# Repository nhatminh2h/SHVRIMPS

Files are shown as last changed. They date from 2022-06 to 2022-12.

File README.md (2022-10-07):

# SHVRIMPS: Synchronised High-Voltage aRbItrary Modular Power Supply

SHVRIMPS is a high-voltage generator and optical imaging setup, capable of
- Outputting arbitrary high-voltage waveforms with an amplitude of 15 kV and a rise time less than 10 ms for load resistances below 8 MΩ.
- Eight independent synchronous and asynchronous 16-bit output channels.
- Monitoring the output high voltages and currents at adjustable sampling rate. Maximum rate of 9875 samples per second.
- Recording video of samples at a rate of 120 fps at 640x480 pixels.
- Displaying live video feed, control panel, and monitoring data on a GUI, accessible over Ethernet.



It consists of three main components: 1) an imaging system based on a Raspberry Pi 4B with a camera, producing a live video stream 2) a DAQ board compatible with either Arduino Nano 33 BLE or ESP32 DevKitC, and c) a multi-channel arbitrary waveform HV supply.

The repository is structured as follows:
- demonstration: videos and matlab figures
- diagrams: block diagrams of the entire setup and individual components
- hardware: KiCAD files showing the PCB design files
- setup: setup files
- software: source files for the Pi and DAQ board

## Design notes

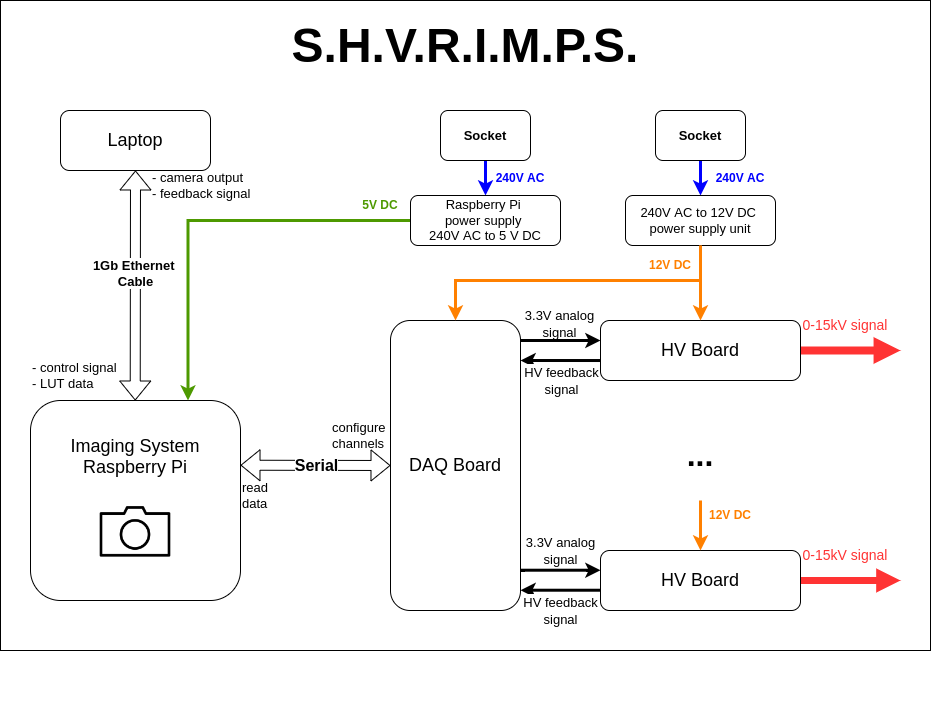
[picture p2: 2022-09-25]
diagrams/General_overview.png

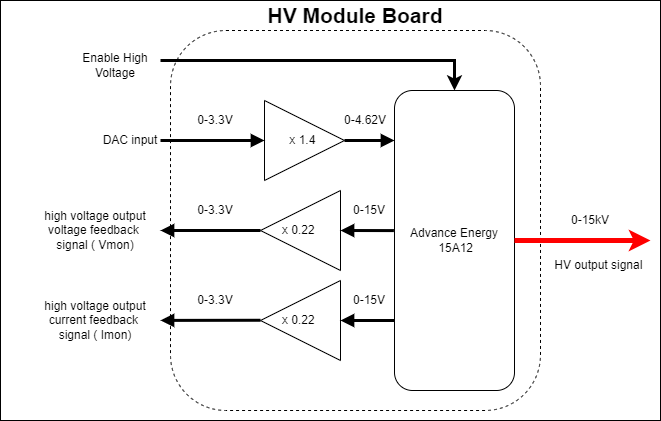
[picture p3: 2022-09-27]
diagrams/HV_module.drawio.png

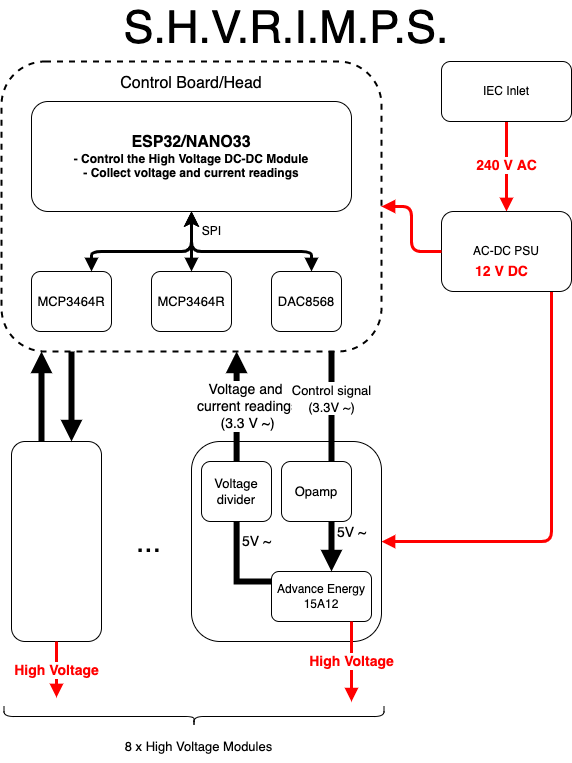
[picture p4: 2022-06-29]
diagrams/SHVRIMPS.png

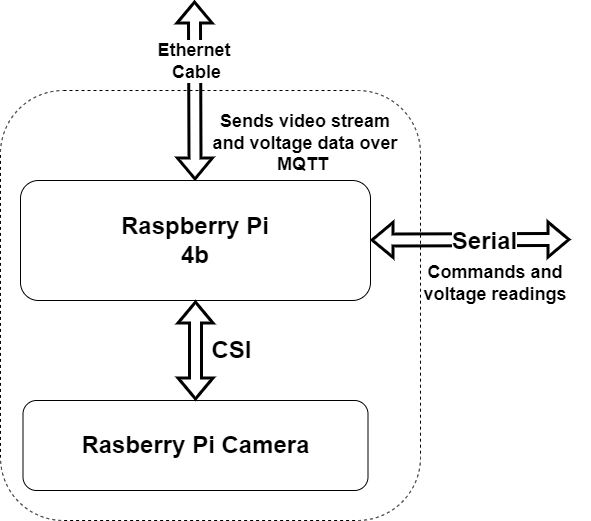
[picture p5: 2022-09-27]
diagrams/Imaging_system.drawio.png

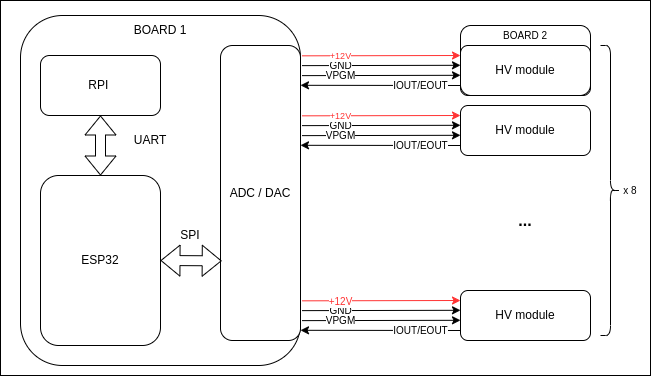
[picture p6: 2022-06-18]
diagrams/diagram.drawio.png

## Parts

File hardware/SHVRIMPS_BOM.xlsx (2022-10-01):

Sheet: DAQ Module
Ref | Qnty | Value | Description | Vendor | Manufacture number | Alternative Option | Unit Price | Total Price
A1, | 1 | Arduino_Nano_v3.x | Arduino Nano 33 BLE | https://uk.rs-online.com/web/p/arduino/1927587 | ABX00030 |  | £25.86 | £25.86
C1, C2, C4, C5, C6, C7, C11, C15, C16, C17, C18, C20, C22, | 13 | 0.1uF | Capacitor_SMD_0805 | https://www.mouser.co.uk/ProductDetail/Vishay-Vitramon/VJ0805Y104JXAMR | VJ0805Y104JXAMR | SMD components of same value | £0.34 | £4.47
C3, C8, C9, C19, C21, | 5 | 10uF | Capacitor_SMD_0806 | https://www.mouser.co.uk/ProductDetail/KYOCERA-AVX/0805ZD106KAT2A?qs=yeMJfaiNeLw5cKDoZRokwQ%3D%3D | 0805ZD106KAT2A | SMD components of same value | £0.18 | £0.88
C10, C12, | 2 | 2.2uF | Capacitor_SMD_0807 | https://www.mouser.co.uk/ProductDetail/KEMET/C0805C225K3RACAUTO |  | SMD components of same value | £0.24 | £0.49
C13, | 1 | 1nF | Capacitor_SMD_0808 | https://www.mouser.co.uk/ProductDetail/KYOCERA-AVX/08055A102JAT2A?qs=zdK0ZDdZmgzNLTxlxqGBmA%3D%3D |  | SMD components of same value | £0.11 | £0.11
C14, | 1 | 1uF | Capacitor_SMD_0809 | https://www.mouser.co.uk/ProductDetail/KYOCERA-AVX/0805DC105KAT2A |  | SMD components of same value | £0.18 | £0.18
D1, | 1 | SM4004 | 400V 1A General Purpose Rectifier Diode, MELF | https://eu.mouser.com/ProductDetail/Rectron/FM4004-W?qs=Iw9Ubr57Px3IHNH1bE4l9w%3D%3D | FM4004-W | SMD components of same value | £0.25 | £0.25
J1, | 1 | Conn_01x03_Male | Single row, 01x03, 2.54mm pitch | https://www.mouser.co.uk/ProductDetail/Molex/90136-1303?qs=kEwmkoUtv7SgZaNi9mb9yw%3D%3D | 90136-1303 | 2.54mm pitch connectors | £1.45 | £1.45
 | 1 | Conn_01x03_Female | Receptacle | https://www.mouser.co.uk/ProductDetail/Molex/90156-0143?qs=jBHU5RPckUpfJXnz3n%2F%2Fgw%3D%3D | 90156-0143 | 2.54mm pitch connectors | £0.54 | £0.54
J2, J3, J4, | 3 | Conn_02x08_Male | Double row, 02x08, 2.54mm pitch | https://www.mouser.co.uk/ProductDetail/Molex/90130-1316?qs=pAYFZ4D%2FDKtl%252BFLAfFoqpw%3D%3D | 90130-1316 | 2.54mm pitch connectors | £4.29 | £12.87
 | 3 | Conn_02x08_Female |  | https://www.mouser.co.uk/ProductDetail/Molex/90142-0016?qs=kEwmkoUtv7Tg2H5guvFtvw%3D%3D | 90142-0016 | 2.54mm pitch connectors | £1.24 | £3.72
J5, | 1 | Conn_01x02_Male | Single row, 01x02, 2.54mm pitch | https://www.mouser.co.uk/ProductDetail/Molex/90136-1202?qs=zF2Np9wwC%252B7fqKXQTHeKiQ%3D%3D | 90136-1202 | 2.54mm pitch connectors | £1.14 | £1.14
 | 1 | Conn_01x02_Female |  | https://www.mouser.co.uk/ProductDetail/Molex/90156-0142?qs=jBHU5RPckUotmv8DXiRxUw%3D%3D | 90156-0142 | 2.54mm pitch connectors | £0.39 | £0.39
R1, R3, R4, | 3 | 0 Ohm | Resistor_SMD_0803 | https://www.mouser.co.uk/ProductDetail/Vishay-Dale/CRCW08050000Z0EAC?qs=E3Y5ESvWgWMnvHb9ZvShmA%3D%3D | CRCW08050000Z0EAC | SMD components of same value | £0.08 | £0.25
R2, | 1 | 50 Ohm | Resistor_SMD_0804 | https://uk.farnell.com/panasonic/era6aeb49r9v/res-0805-49r9-0-125w-metal-film/dp/1810372 | ERA6AEB49R9V | SMD components of same value | £0.25 | £0.25
R5, R6, | 2 | 100k Ohm | Resistor_SMD_0805 | https://www.mouser.co.uk/ProductDetail/Vishay-Dale/RCS0805100KFKEA?qs=NKmfXavxMay%252BH0mbX9hKBw%3D%3D |  | SMD components of same value | £0.20 | £0.40
U1, | 1 | ESP32-DevKit-C | Alternative microcontroller: ESP32-devkitC-v4 |  |  |  |  | £0.00
U2, | 1 | LM7805_TO220 | Positive 1A 35V Linear Regulator, Fixed Output 5V, TO-220-3 | https://uk.farnell.com/stmicroelectronics/l7805abv/ic-v-reg-5v/dp/1467758?st=7805 | L7805ABV |  | £0.72 | £0.72
U3, | 1 | MCP1754S-3302xCB | Fixed 150mA Low Dropout Voltage Regulator, Positive, 3.3V output, SOT-23 | https://uk.rs-online.com/web/p/voltage-regulators/7559521 | MCP1754ST-3302E/CB | LDO with the same specification and footprint(make note of the pin out as different manufacturers have different ordering). | £0.45 | £0.45
U4, | 1 | MCP1825S-3.3V | 500mA, Low-Voltage, Low Quiescent Current LDO Regulator, SOT-223-3 | https://www.mouser.co.uk/ProductDetail/Microchip-Technology-Atmel/MCP1825ST-3302E-DB?qs=gsqZ4L1luKpq7RsgmIaiQQ%3D%3D | MCP1825ST-3302E/DB | LDO with the same specification and footprint(make note of the pin out as different manufacturers have different ordering). | £0.58 | £0.58
U5, | 1 | MCP1501-33xSN | 3.3V, 0.1%, 20mA, Precision Voltage Reference, SOIC-8 | https://uk.farnell.com/microchip/mcp1501-30e-sn/voltage-ref-series-3v-nsoic-8/dp/2524552?st=mcp1501 | MCP1501-30E/SN | LDO with the same specification and footprint(make note of the pin out as different manufacturers have different ordering). | £1.29 | £1.29
U6, U7, | 2 | MCP3464R | TSSOP-20_4.4x6.5mm_P0.65mm | https://www.mouser.co.uk/ProductDetail/Microchip-Technology/MCP3464R-E-ST?qs=W%2FMpXkg%252BdQ5bjobVCBkOgQ%3D%3D | MCP3464R-E/ST | MCP3x6x family | £4.38 | £8.76
U8, | 1 | DAC8568IAPW | TSSOP-16- | https://www.mouser.co.uk/ProductDetail/Texas-Instruments/DAC8568IAPW?qs=JxdSYA%2FPj%252BEQdFVS13frJg%3D%3D | DAC8568IAPW | DAC856x family | £21.65 | £21.65
X1, | 1 | ECS-2520MVLC-049-BN-TR | HCMOS Crystal Clock Oscillator, 2.5x2.0 mm SMD | https://www.mouser.co.uk/ProductDetail/ECS/ECS-2520MVLC-049-BN-TR?qs=DPoM0jnrROWa%252BbOCdP2Nhw%3D%3D | ECS-2520MVLC-049-BN-TR | Oscillator with frequency under 20 MHz and similar footprint. | £1.17 | £1.17
 | 1 | PCB | 4-Layer PCB | JLC-PCB |  |  | £1.31 | £1.31
 | 1 | PCB Stencil | Thin sheet of metal masking for solder paste application | JLC-PCB |  |  | £10
 |  |  |  |  |  |  | Total | £89.18

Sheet: HV Board
NOTE: The following BOM is for ONE high voltage module
Ref | Qnty | Value | Description | Vendor | Manufacture number | Alternative Option | Unit Price | Total Price
C1, C2, C3 | 3 | 0.1uF | Unpolarized capacitor | https://www.mouser.co.uk/ProductDetail/Vishay-BC-Components/K104M10X7RF5UH5?qs=uwenMUmGrtfrBFUqL2dLRw%3D%3D |  |  | 0.193 | 0.579
D1, | 1 | TZX3V6A-TR | Zener diode | https://www.mouser.co.uk/ProductDetail/Vishay-Semiconductors/ZPY16-TR?qs=6Fe8ASSgjNtFiGayzk%2F7%252BQ%3D%3D |  |  | 0.319 | 0.319
D2, | 1 | LED | Light emitting diode | https://www.mouser.co.uk/ProductDetail/VCC/VAOL-3MAE2?qs=io7aH2hdVh6UJW4IWVOfMg%3D%3D |  |  | 0.462 | 0.462
J1, | 1 | Conn_02x05_Male | Single row, 02x05, 2.54mm pitch | https://www.mouser.co.uk/ProductDetail/Molex/90142-0010?qs=BLN8Q0P37WbAKoqIAY0hgw%3D%3D | 90142-0010 |  | 0.756 | 0.756
J1- | 1 | Conn_02x05_Female | Receptacle | https://www.mouser.co.uk/ProductDetail/Molex/90130-1210?qs=FqTglUE30jKws6eRab4Phg%3D%3D | 90130-1210 |  | 1.81 | 1.81
J3, | 1 | Conn_01x02_Male | Single row, 01x02, 2.54mm pitch | https://www.mouser.co.uk/ProductDetail/Molex/90136-1202?qs=zF2Np9wwC%252B7fqKXQTHeKiQ%3D%3D | 90136-1202 |  | 1.14 | 1.14
J3- | 1 | Conn_01x02_Female | Receptacle | https://www.mouser.co.uk/ProductDetail/Molex/90156-0142?qs=jBHU5RPckUotmv8DXiRxUw%3D%3D | 90156-0142 |  | 0.386 | 0.386
R1, | 1 | 4.7k | Resistor | https://www.mouser.co.uk/ProductDetail/YAGEO/MFR-25FBF52-4K7?qs=oAGoVhmvjhyEuU2iU0uA4w%3D%3D | MFR-25FBF52-4K7 |  | 0.025 | 0.025
R2, | 2 | 2k | Resistor | https://www.mouser.co.uk/ProductDetail/YAGEO/MFR-12FTF52-2K?qs=oAGoVhmvjhwaGCFyQGkulg%3D%3D | MFR-25FBF52-4K7 |  | 0.021 | 0.042
R3, | 1 | 10k | Resistor | https://www.mouser.co.uk/ProductDetail/YAGEO/MFR-12FTF52-10K?qs=oAGoVhmvjhzLlUYKKBtdYQ%3D%3D | MFR-12FTF52-10K |  | 0.084 | 0.084
R5, R7, | 2 | 390k | Resistor | https://www.mouser.co.uk/ProductDetail/Vishay-BC-Components/HVR2500003903FR500?qs=7DG%2Fna1Fp6tcZrbH7PbgIQ%3D%3D |  |  | 0.353 | 0.706
R6, R8, | 2 | 110k | Resistor | https://www.mouser.co.uk/ProductDetail/Vishay-Dale/CPF110K000FKEE6 |  |  | 0.664 | 1.328
U1, | 1 | LM7809_TO220 | Positive 1A 35V Linear Regulator, Fixed Output 9V, TO-220-3 | https://www.mouser.co.uk/ProductDetail/STMicroelectronics/L7809ABV?qs=arR7071FstcxVp1H1MGQ%2Fw%3D%3D | L7809ABV |  | 0.655 | 0.655
U2, | 1 | LM358 | Dual Low-Noise Operational Amplifiers, DIP-8 | https://www.mouser.co.uk/ProductDetail/Texas-Instruments/LM358AP?qs=Zu35EjizYSShld7Gr9Muww%3D%3D | LM358AP |  | 0.353 | 0.353
U3, | 1 | 15A12 | High Voltage DC-DC module | https://www.mouser.co.uk/ProductDetail/Advanced-Energy/15A12-P4?qs=BZBei1rCqCD%252BiPNKsMykyg%3D%3D |  | Other | 433.09 | 433.09
 | 1 | PCB | 2-Layer PCB | JLC-PCB |  |  | 2 | 2
 |  |  |  |  |  |  | Total | 443.735
 |  |  |  |  |  |  | Total for 8 boards | 3549.88

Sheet: Raspberry Pi + camera
Ref | Qnty | Value | Description | Vendor | Manufacture number | Alternative Option | Unit Price | Total Price
 | 1 |  | Raspberry Pi 4B | https://www.raspberrypi.com/products/raspberry-pi-4-model-b/ |  |  | £65 | £65
 | 1 |  | Pi Camera v2 | https://thepihut.com/products/raspberry-pi-camera-module?src=raspberrypi |  |  | £26 | £26
 | 1 |  | Pi Screen
 |  |  |  |  |  |  | Total | £91

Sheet: Wires and Consumables
Ref | Qnty | Value | Description | Vendor | Manufacture number | Alternative Option | Unit Price | Total Price
 | 1 | CHIPQUIK SMD291SN Lead Free Solder Paste, 35g Syringe | Solder paste | https://uk.rs-online.com/web/p/solder-pastes/1466194 |  |  | £40.25 | £40.25
 | 1 | CHIPQUIK SMD291 10g Lead Free Solder Flux Syringe | Solder Flux | https://uk.rs-online.com/web/p/solder-flux/1466649 |  |  | £16.88 | £16.88
 | 1 | Mueller Electric WI-M / Silicone Wire Series Black 0.82 mm² Hook Up Wire, 18 AWG, 7/59/.05 mm, 3.05m, Silicone | Wire for internal wiring | https://uk.rs-online.com/web/p/hook-up-wire/2431647 |  |  | £18.62 | £18.62
 |  |  |  |  |  |  | Total | £75.75

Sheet: Enclosure and Mains Supply
Ref | Qnty | Value | Description | Vendor | Manufacture number | Unit Price | Total Price

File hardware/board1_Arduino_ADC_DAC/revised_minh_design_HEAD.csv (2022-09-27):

Source: | /Users/user/SHVRIMPS/SHVRIMPS/hardware/board1_Arduino_ADC_DAC/revised_minh_design.kicad_sch
Date: | Saturday, 24 September 2022 at 17:24:06
Tool: | Eeschema (6.0.5-0)
Generator: | /Applications/KiCad/KiCad.app/Contents/SharedSupport/plugins/bom_csv_grouped_by_value.py
Component Count: | 45
Individual Components:
Item | Qty | Reference(s) | Value | LibPart | Footprint | Datasheet
 |  | A1 | Arduino_Nano_v3.x | MCU_Module:Arduino_Nano_v3.x | Module:Arduino_Nano | http://www.mouser.com/pdfdocs/Gravitech_Arduino_Nano3_0.pdf
 |  | C1 | 0.1uF | Device:C | Capacitor_SMD:C_0805_2012Metric_Pad1.18x1.45mm_HandSolder | ~
 |  | C2 | 0.1uF | Device:C | Capacitor_SMD:C_0805_2012Metric_Pad1.18x1.45mm_HandSolder | ~
 |  | C3 | 10uF | Device:C | Capacitor_SMD:C_0805_2012Metric_Pad1.18x1.45mm_HandSolder | ~
 |  | C4 | 0.1uF | Device:C | Capacitor_SMD:C_0805_2012Metric_Pad1.18x1.45mm_HandSolder | ~
 |  | C5 | 0.1uF | Device:C | Capacitor_SMD:C_0805_2012Metric_Pad1.18x1.45mm_HandSolder | ~
 |  | C6 | 0.1uF | Device:C | Capacitor_SMD:C_0805_2012Metric_Pad1.18x1.45mm_HandSolder | ~
 |  | C7 | 0.1uF | Device:C | Capacitor_SMD:C_0805_2012Metric_Pad1.18x1.45mm_HandSolder | ~
 |  | C8 | 10uF | Device:C | Capacitor_SMD:C_0805_2012Metric_Pad1.18x1.45mm_HandSolder | ~
 |  | C9 | 10uF | Device:C | Capacitor_SMD:C_0805_2012Metric_Pad1.18x1.45mm_HandSolder | ~
 |  | C10 | 2.2uF | Device:C | Capacitor_SMD:C_0805_2012Metric_Pad1.18x1.45mm_HandSolder | ~
 |  | C11 | 0.1uF | Device:C | Capacitor_SMD:C_0805_2012Metric_Pad1.18x1.45mm_HandSolder | ~
 |  | C12 | 2.2uF | Device:C | Capacitor_SMD:C_0805_2012Metric_Pad1.18x1.45mm_HandSolder | ~
 |  | C13 | 1nF | Device:C | Capacitor_SMD:C_0805_2012Metric_Pad1.18x1.45mm_HandSolder | ~
 |  | C14 | 1uF | Device:C | Capacitor_SMD:C_0805_2012Metric_Pad1.18x1.45mm_HandSolder | ~
 |  | C15 | 0.1uF | Device:C | Capacitor_SMD:C_0805_2012Metric_Pad1.18x1.45mm_HandSolder | ~
 |  | C16 | 0.1uF | Device:C | Capacitor_SMD:C_0805_2012Metric_Pad1.18x1.45mm_HandSolder | ~
 |  | C17 | 0.1uF | Device:C | Capacitor_SMD:C_0805_2012Metric_Pad1.18x1.45mm_HandSolder | ~
 |  | C18 | 0.1uF | Device:C | Capacitor_SMD:C_0805_2012Metric_Pad1.18x1.45mm_HandSolder | ~
 |  | C19 | 10uF | Device:C | Capacitor_SMD:C_0805_2012Metric_Pad1.18x1.45mm_HandSolder | ~
 |  | C20 | 0.1uF | Device:C | Capacitor_SMD:C_0805_2012Metric_Pad1.18x1.45mm_HandSolder | ~
 |  | C21 | 10uF | Device:C | Capacitor_SMD:C_0805_2012Metric_Pad1.18x1.45mm_HandSolder | ~
 |  | C22 | 0.1uF | Device:C | Capacitor_SMD:C_0805_2012Metric_Pad1.18x1.45mm_HandSolder | ~
 |  | D1 | SM4004 | Diode:SM4004 | Diode_SMD:D_MELF | http://cdn-reichelt.de/documents/datenblatt/A400/SMD1N400%23DIO.pdf
 |  | J1 | Conn_01x03_Male | Connector:Conn_01x03_Male | Connector_PinSocket_2.54mm:PinSocket_1x03_P2.54mm_Vertical | ~
 |  | J2 | Conn_02x08_Odd_Even | Connector_Generic:Conn_02x08_Odd_Even | Connector_PinSocket_2.54mm:PinSocket_2x08_P2.54mm_Vertical | ~
 |  | J3 | Conn_02x08_Odd_Even | Connector_Generic:Conn_02x08_Odd_Even | Connector_PinSocket_2.54mm:PinSocket_2x08_P2.54mm_Vertical | ~
 |  | J4 | Conn_02x08_Odd_Even | Connector_Generic:Conn_02x08_Odd_Even | Connector_PinSocket_2.54mm:PinSocket_2x08_P2.54mm_Vertical | ~
 |  | J5 | Conn_01x02_Male | Connector:Conn_01x02_Male | Connector_PinSocket_2.54mm:PinSocket_1x02_P2.54mm_Vertical | ~
 |  | R1 | 0 | Device:R | Resistor_SMD:R_0805_2012Metric_Pad1.20x1.40mm_HandSolder | ~
 |  | R2 | 50 | Device:R | Resistor_SMD:R_0805_2012Metric_Pad1.20x1.40mm_HandSolder | ~
 |  | R3 | 0 | Device:R | Resistor_SMD:R_0805_2012Metric_Pad1.20x1.40mm_HandSolder | ~
 |  | R4 | 0 | Device:R | Resistor_SMD:R_0805_2012Metric_Pad1.20x1.40mm_HandSolder | ~
 |  | R5 | 100k | Device:R | Resistor_SMD:R_0805_2012Metric_Pad1.20x1.40mm_HandSolder | ~
 |  | R6 | 100k | Device:R | Resistor_SMD:R_0805_2012Metric_Pad1.20x1.40mm_HandSolder | ~
 |  | TP1 | TestPoint | Connector:TestPoint | Connector_PinHeader_2.54mm:PinHeader_1x01_P2.54mm_Vertical | ~
 |  | U1 | ESP32-DevKit-C | design:ESP32-DevKit-C | Library:ESP32-devkitC-v4
 |  | U2 | LM7805_TO220 | Regulator_Linear:LM7805_TO220 | Package_TO_SOT_THT:TO-220-3_Vertical | https://www.onsemi.cn/PowerSolutions/document/MC7800-D.PDF
 |  | U3 | MCP1754S-3302xCB | Regulator_Linear:MCP1754S-3302xCB | Package_TO_SOT_SMD:SOT-23 | http://ww1.microchip.com/downloads/en/DeviceDoc/20002276C.pdf
 |  | U4 | MCP1825S-3.3V | Regulator_Linear:MCP1825S | Package_TO_SOT_SMD:SOT-223-3_TabPin2 | http://ww1.microchip.com/downloads/en/devicedoc/22056b.pdf
 |  | U5 | MCP1501-33xSN | Reference_Voltage:MCP1501-33xSN | Package_SO:SOIC-8_3.9x4.9mm_P1.27mm | http://ww1.microchip.com/downloads/en/DeviceDoc/20005474E.pdf
 |  | U6 | MCP3464R | design:MCP3464R | Package_SO:TSSOP-20_4.4x6.5mm_P0.65mm
 |  | U7 | MCP3464R | design:MCP3464R | Package_SO:TSSOP-20_4.4x6.5mm_P0.65mm
 |  | U8 | DAC8568IAPW | design:DAC8568IAPW | Package_SO:TSSOP-16-1EP_4.4x5mm_P0.65mm
 |  | X1 | ECS-2520MVLC-049-BN-TR | Oscillator:ECS-2520MV-xxx-xx | Oscillator:Oscillator_SMD_ECS_2520MV-xxx-xx-4Pin_2.5x2.0mm | https://www.ecsxtal.com/store/pdf/ECS-2520MV.pdf
Collated Components:
Item | Qty | Reference(s) | Value | LibPart | Footprint | Datasheet
1 | 1 | A1 | Arduino_Nano_v3.x | MCU_Module:Arduino_Nano_v3.x | Module:Arduino_Nano | http://www.mouser.com/pdfdocs/Gravitech_Arduino_Nano3_0.pdf
2 | 13 | C1, C2, C4, C5, C6, C7, C11, C15, C16, C17, C18, C20, C22 | 0.1uF | Device:C | Capacitor_SMD:C_0805_2012Metric_Pad1.18x1.45mm_HandSolder | ~
3 | 5 | C3, C8, C9, C19, C21 | 10uF | Device:C | Capacitor_SMD:C_0805_2012Metric_Pad1.18x1.45mm_HandSolder | ~
4 | 2 | C10, C12 | 2.2uF | Device:C | Capacitor_SMD:C_0805_2012Metric_Pad1.18x1.45mm_HandSolder | ~
5 | 1 | C13 | 1nF | Device:C | Capacitor_SMD:C_0805_2012Metric_Pad1.18x1.45mm_HandSolder | ~
6 | 1 | C14 | 1uF | Device:C | Capacitor_SMD:C_0805_2012Metric_Pad1.18x1.45mm_HandSolder | ~
7 | 1 | D1 | SM4004 | Diode:SM4004 | Diode_SMD:D_MELF | http://cdn-reichelt.de/documents/datenblatt/A400/SMD1N400%23DIO.pdf
8 | 1 | J1 | Conn_01x03_Male | Connector:Conn_01x03_Male | Connector_PinSocket_2.54mm:PinSocket_1x03_P2.54mm_Vertical | ~
9 | 3 | J2, J3, J4 | Conn_02x08_Odd_Even | Connector_Generic:Conn_02x08_Odd_Even | Connector_PinSocket_2.54mm:PinSocket_2x08_P2.54mm_Vertical | ~
10 | 1 | J5 | Conn_01x02_Male | Connector:Conn_01x02_Male | Connector_PinSocket_2.54mm:PinSocket_1x02_P2.54mm_Vertical | ~
11 | 3 | R1, R3, R4 | 0 | Device:R | Resistor_SMD:R_0805_2012Metric_Pad1.20x1.40mm_HandSolder | ~
12 | 1 | R2 | 50 | Device:R | Resistor_SMD:R_0805_2012Metric_Pad1.20x1.40mm_HandSolder | ~
13 | 2 | R5, R6 | 100k | Device:R | Resistor_SMD:R_0805_2012Metric_Pad1.20x1.40mm_HandSolder | ~
14 | 1 | TP1 | TestPoint | Connector:TestPoint | Connector_PinHeader_2.54mm:PinHeader_1x01_P2.54mm_Vertical | ~
15 | 1 | U1 | ESP32-DevKit-C | design:ESP32-DevKit-C | Library:ESP32-devkitC-v4
16 | 1 | U2 | LM7805_TO220 | Regulator_Linear:LM7805_TO220 | Package_TO_SOT_THT:TO-220-3_Vertical | https://www.onsemi.cn/PowerSolutions/document/MC7800-D.PDF
17 | 1 | U3 | MCP1754S-3302xCB | Regulator_Linear:MCP1754S-3302xCB | Package_TO_SOT_SMD:SOT-23 | http://ww1.microchip.com/downloads/en/DeviceDoc/20002276C.pdf
18 | 1 | U4 | MCP1825S-3.3V | Regulator_Linear:MCP1825S | Package_TO_SOT_SMD:SOT-223-3_TabPin2 | http://ww1.microchip.com/downloads/en/devicedoc/22056b.pdf
19 | 1 | U5 | MCP1501-33xSN | Reference_Voltage:MCP1501-33xSN | Package_SO:SOIC-8_3.9x4.9mm_P1.27mm | http://ww1.microchip.com/downloads/en/DeviceDoc/20005474E.pdf
20 | 2 | U6, U7 | MCP3464R | design:MCP3464R | Package_SO:TSSOP-20_4.4x6.5mm_P0.65mm
21 | 1 | U8 | DAC8568IAPW | design:DAC8568IAPW | Package_SO:TSSOP-16-1EP_4.4x5mm_P0.65mm
22 | 1 | X1 | ECS-2520MVLC-049-BN-TR | Oscillator:ECS-2520MV-xxx-xx | Oscillator:Oscillator_SMD_ECS_2520MV-xxx-xx-4Pin_2.5x2.0mm | https://www.ecsxtal.com/store/pdf/ECS-2520MV.pdf

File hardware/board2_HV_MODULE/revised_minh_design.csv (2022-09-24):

Source: | /Users/user/hvawg/board2_HV_MODULE/revised_minh_design.kicad_sch
Date: | Thursday, 30 June 2022 at 15:07:25
Tool: | Eeschema (6.0.5-0)
Generator: | /Applications/KiCad/KiCad.app/Contents/SharedSupport/plugins/bom_csv_grouped_by_value_with_fp.py
Component Count: | 18
Ref | Qnty | Value | Cmp name | Footprint | Description | Vendor
C1, C2, C3, | 3 | 0.1uF | C | Capacitor_THT:C_Disc_D6.0mm_W2.5mm_P5.00mm | Unpolarized capacitor
D1, | 1 | TZX3V6A-TR | D_Zener | Diode_THT:D_DO-35_SOD27_P7.62mm_Horizontal | Zener diode
D2, | 1 | LED | LED | LED_THT:LED_D3.0mm_Clear | Light emitting diode
J1, | 1 | Conn_01x07_Male | Conn_01x07_Male | Connector_PinSocket_2.54mm:PinSocket_1x07_P2.54mm_Vertical | Generic connector, single row, 01x07, script generated (kicad-library-utils/schlib/autogen/connector/)
J2, | 1 | Conn_01x01_Male | Conn_01x01_Male | Connector_Wire:SolderWire-0.75sqmm_1x01_D1.25mm_OD2.3mm_Relief | Generic connector, single row, 01x01, script generated (kicad-library-utils/schlib/autogen/connector/)
R1, R3, | 2 | 10k | R | Resistor_THT:R_Axial_DIN0207_L6.3mm_D2.5mm_P10.16mm_Horizontal | Resistor
R2, | 1 | 4.7k | R | Resistor_THT:R_Axial_DIN0207_L6.3mm_D2.5mm_P7.62mm_Horizontal | Resistor
R4, | 1 | 1K | R | Resistor_THT:R_Axial_DIN0207_L6.3mm_D2.5mm_P10.16mm_Horizontal | Resistor
R5, | 1 | 2K | R | Resistor_THT:R_Axial_DIN0207_L6.3mm_D2.5mm_P15.24mm_Horizontal | Resistor
R6, R8, | 2 | 1.1K | R | Resistor_THT:R_Axial_DIN0207_L6.3mm_D2.5mm_P10.16mm_Horizontal | Resistor
R7, | 1 | 2K | R | Resistor_THT:R_Axial_DIN0207_L6.3mm_D2.5mm_P10.16mm_Horizontal | Resistor
U1, | 1 | LM7805_TO220 | LM7805_TO220 | Package_TO_SOT_THT:TO-220-3_Vertical | Positive 1A 35V Linear Regulator, Fixed Output 5V, TO-220
U2, | 1 | NE5532 | NE5532 | Package_DIP:DIP-8_W7.62mm | Dual Low-Noise Operational Amplifiers, DIP-8/SOIC-8
U3, | 1 | CB101 | CB101 | Library:CB101

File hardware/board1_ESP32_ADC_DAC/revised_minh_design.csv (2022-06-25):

Source: | /Users/user/hvawg/board1_ESP32_ADC_DAC/revised_minh_design.kicad_sch
Date: | Friday, 24 June 2022 at 15:34:22
Tool: | Eeschema (6.0.5-0)
Generator: | /Applications/KiCad/KiCad.app/Contents/SharedSupport/plugins/bom_csv_grouped_by_value_with_fp.py
Component Count: | 34
Ref | Qnty | Value | Cmp name | Footprint | Description | Vendor
C1, C2, C4, C5, C6, C7, C11, C15, C16, C17, C18, | 11 | 0.1uF | C | Capacitor_SMD:C_0805_2012Metric_Pad1.18x1.45mm_HandSolder | Unpolarized capacitor
C3, C8, C9, | 3 | 10uF | C | Capacitor_SMD:C_0805_2012Metric_Pad1.18x1.45mm_HandSolder | Unpolarized capacitor
C10, C12, | 2 | 2.2uF | C | Capacitor_SMD:C_0805_2012Metric_Pad1.18x1.45mm_HandSolder | Unpolarized capacitor
C13, | 1 | 1nF | C | Capacitor_SMD:C_0805_2012Metric_Pad1.18x1.45mm_HandSolder | Unpolarized capacitor
C14, | 1 | 1uF | C | Capacitor_SMD:C_0805_2012Metric_Pad1.18x1.45mm_HandSolder | Unpolarized capacitor
J1, | 1 | Conn_01x03_Male | Conn_01x03_Male | Connector_PinSocket_2.54mm:PinSocket_1x03_P2.54mm_Vertical | Generic connector, single row, 01x03, script generated (kicad-library-utils/schlib/autogen/connector/)
J2, J3, J4, | 3 | Conn_01x08_Male | Conn_01x08_Male | Connector_PinSocket_2.54mm:PinSocket_1x08_P2.54mm_Vertical | Generic connector, single row, 01x08, script generated (kicad-library-utils/schlib/autogen/connector/)
R1, R3, | 2 | 0 | R | Resistor_SMD:R_0805_2012Metric_Pad1.20x1.40mm_HandSolder | Resistor
R2, | 1 | 50 | R | Resistor_SMD:R_0805_2012Metric_Pad1.20x1.40mm_HandSolder | Resistor
U1, | 1 | ESP32-DevKit-C | ESP32-DevKit-C | Library:ESP32-devkitC-v4
U2, | 1 | LM7805_TO220 | LM7805_TO220 | Package_TO_SOT_THT:TO-220-3_Vertical | Positive 1A 35V Linear Regulator, Fixed Output 5V, TO-220
U3, | 1 | MCP1754S-3302xCB | MCP1754S-3302xCB | Package_TO_SOT_SMD:SOT-23 | Fixed 150mA Low Dropout Voltage Regulator, Positive, 3.3V output, SOT-23
U4, | 1 | MCP1825S-3.3V | MCP1825S | Package_TO_SOT_SMD:SOT-223-3_TabPin2 | 500mA, Low-Voltage, Low Quiescent Current LDO Regulator, SOT-223, TO-220, TO-263
U5, | 1 | MCP1501-33xSN | MCP1501-33xSN | Package_SO:SOIC-8_3.9x4.9mm_P1.27mm | 3.3V, 0.1%, 20mA, Precision Voltage Reference, SOIC-8
U6, U7, | 2 | MCP3464R | MCP3464R | Package_SO:TSSOP-20_4.4x6.5mm_P0.65mm
U8, | 1 | DAC8568IAPW | DAC8568IAPW | Package_SO:TSSOP-16-1EP_4.4x5mm_P0.65mm
X1, | 1 | ECS-2520MVLC-049-BN-TR | ECS-2520MV-xxx-xx | Oscillator:Oscillator_SMD_ECS_2520MV-xxx-xx-4Pin_2.5x2.0mm | HCMOS Crystal Clock Oscillator, 2.5x2.0 mm SMD

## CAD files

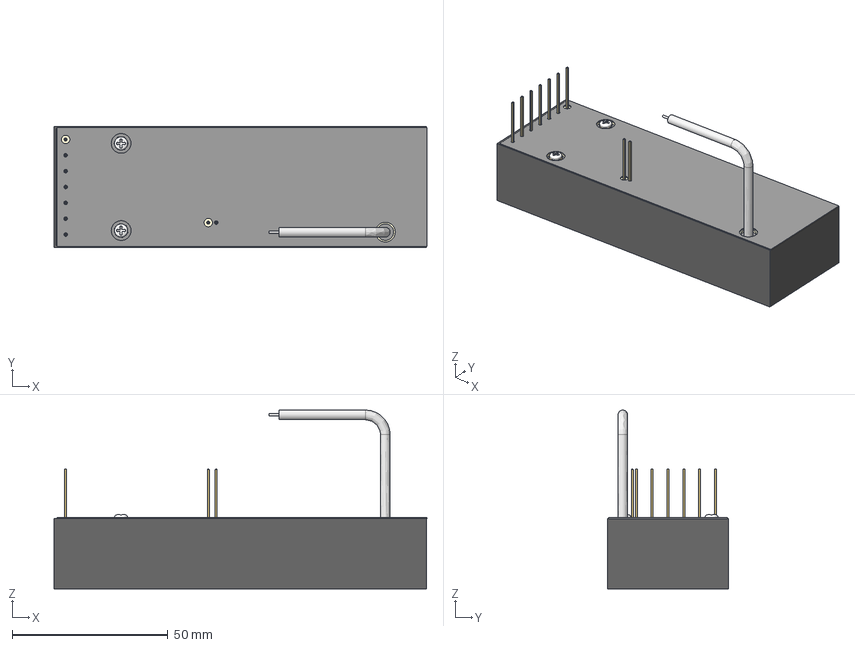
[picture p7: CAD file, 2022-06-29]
diagrams/OL-015_15A_STANDARD.stp
119.6 x 38.7 x 57.4 mm

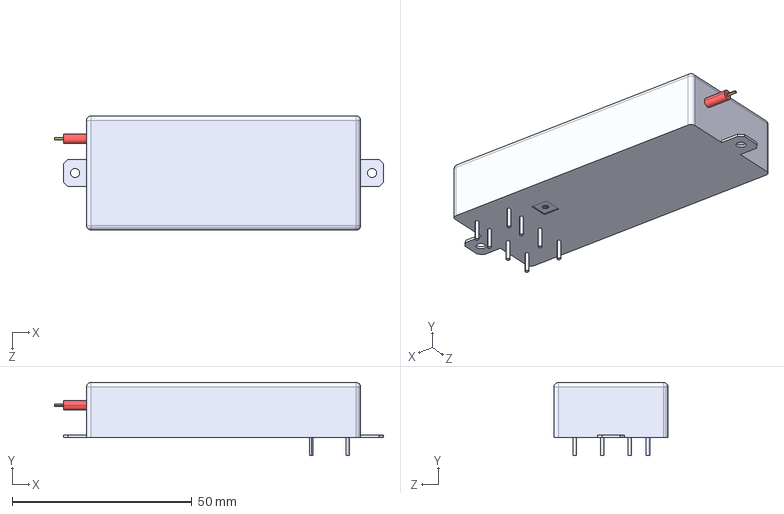
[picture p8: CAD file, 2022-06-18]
hardware/board1_Arduino_ADC_DAC/CB101.STEP
91.4 x 20.3 x 31.8 mm

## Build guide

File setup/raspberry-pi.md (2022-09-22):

nmap -n -sP 10.42.0.255/24
ssh pi@10.42.0.198

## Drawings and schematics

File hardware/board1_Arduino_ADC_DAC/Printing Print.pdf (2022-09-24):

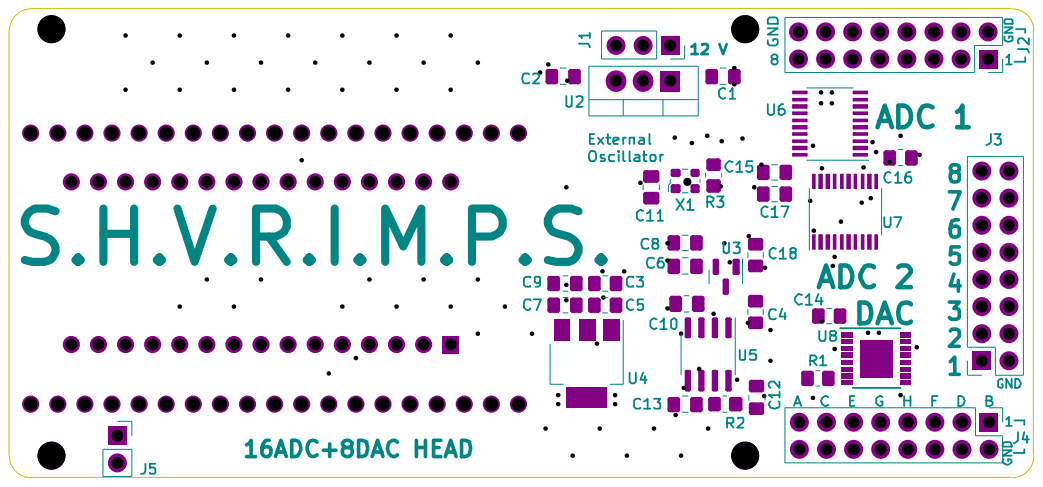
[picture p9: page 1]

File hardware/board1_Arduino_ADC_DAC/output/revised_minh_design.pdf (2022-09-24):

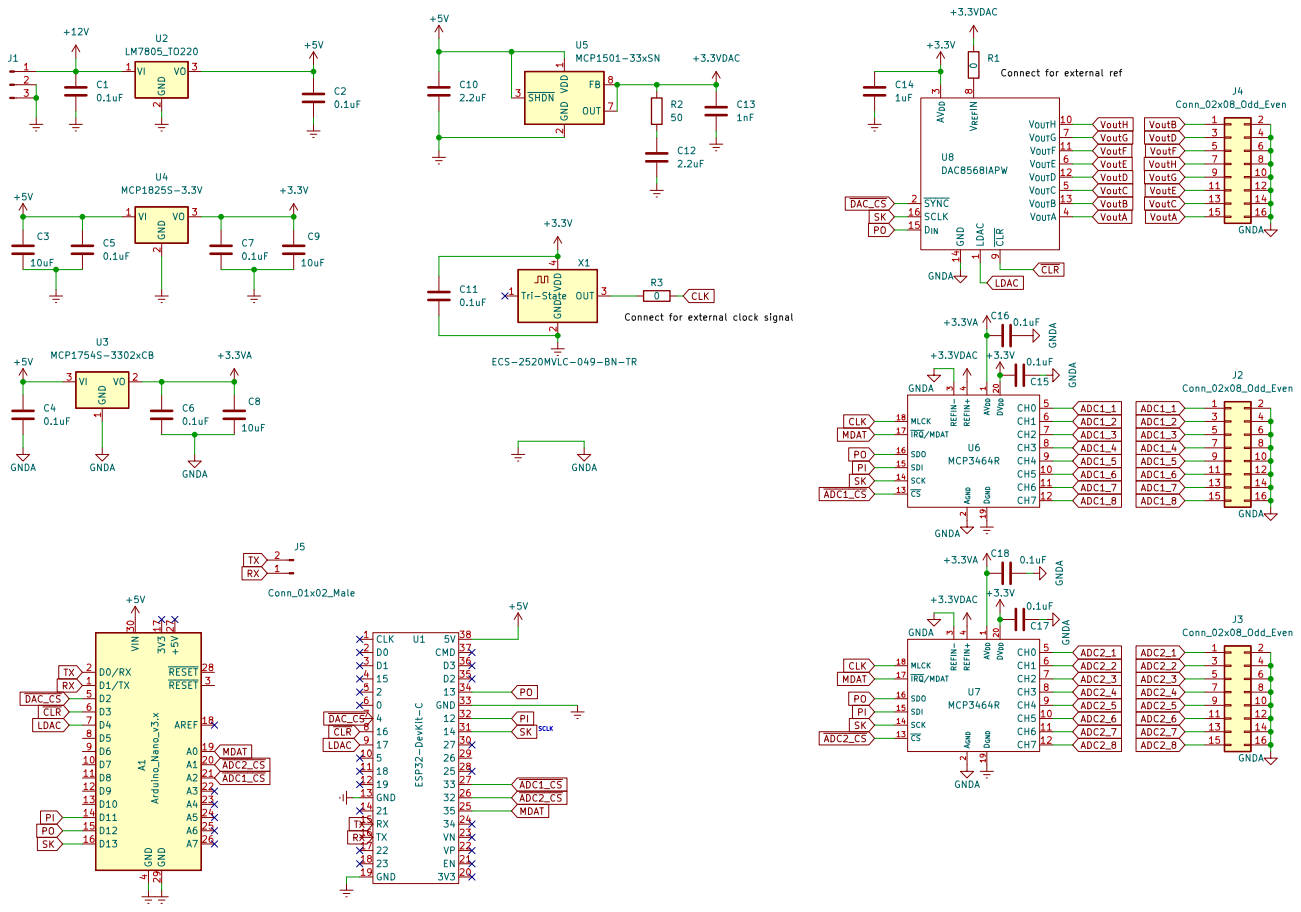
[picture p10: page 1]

2 ~{SHDN} 3 OUT 7 FB 8 U5MCP1501-33xSN GNDA

1 V_{OUT}H 10 V_{OUT}F 11 V_{OUT}D 12 V_{OUT}B 13 GND 14

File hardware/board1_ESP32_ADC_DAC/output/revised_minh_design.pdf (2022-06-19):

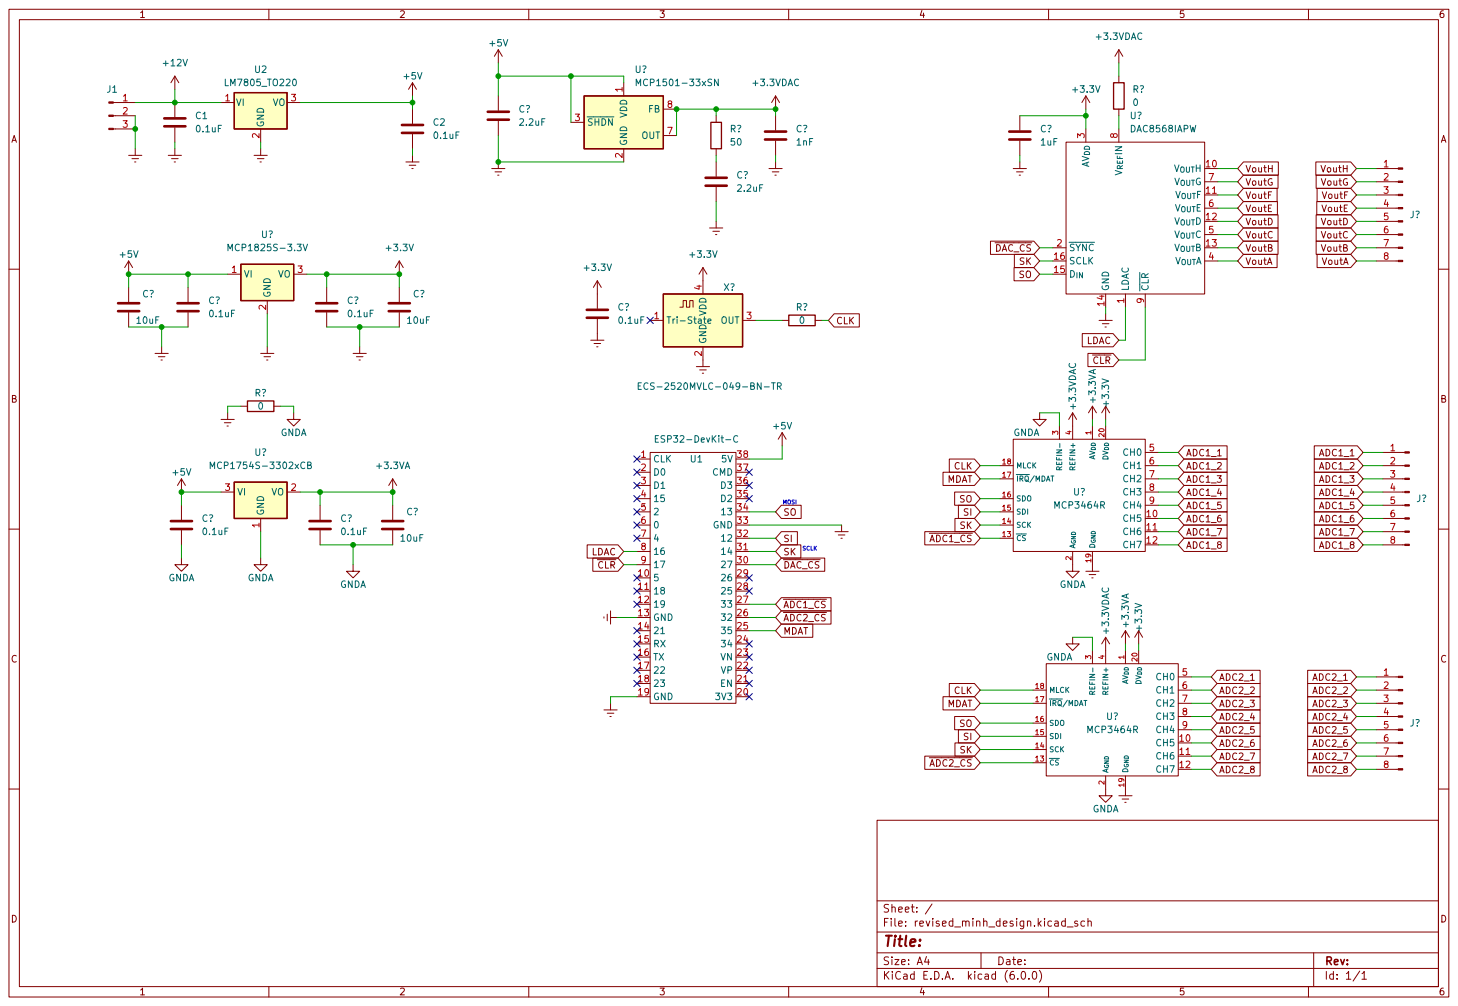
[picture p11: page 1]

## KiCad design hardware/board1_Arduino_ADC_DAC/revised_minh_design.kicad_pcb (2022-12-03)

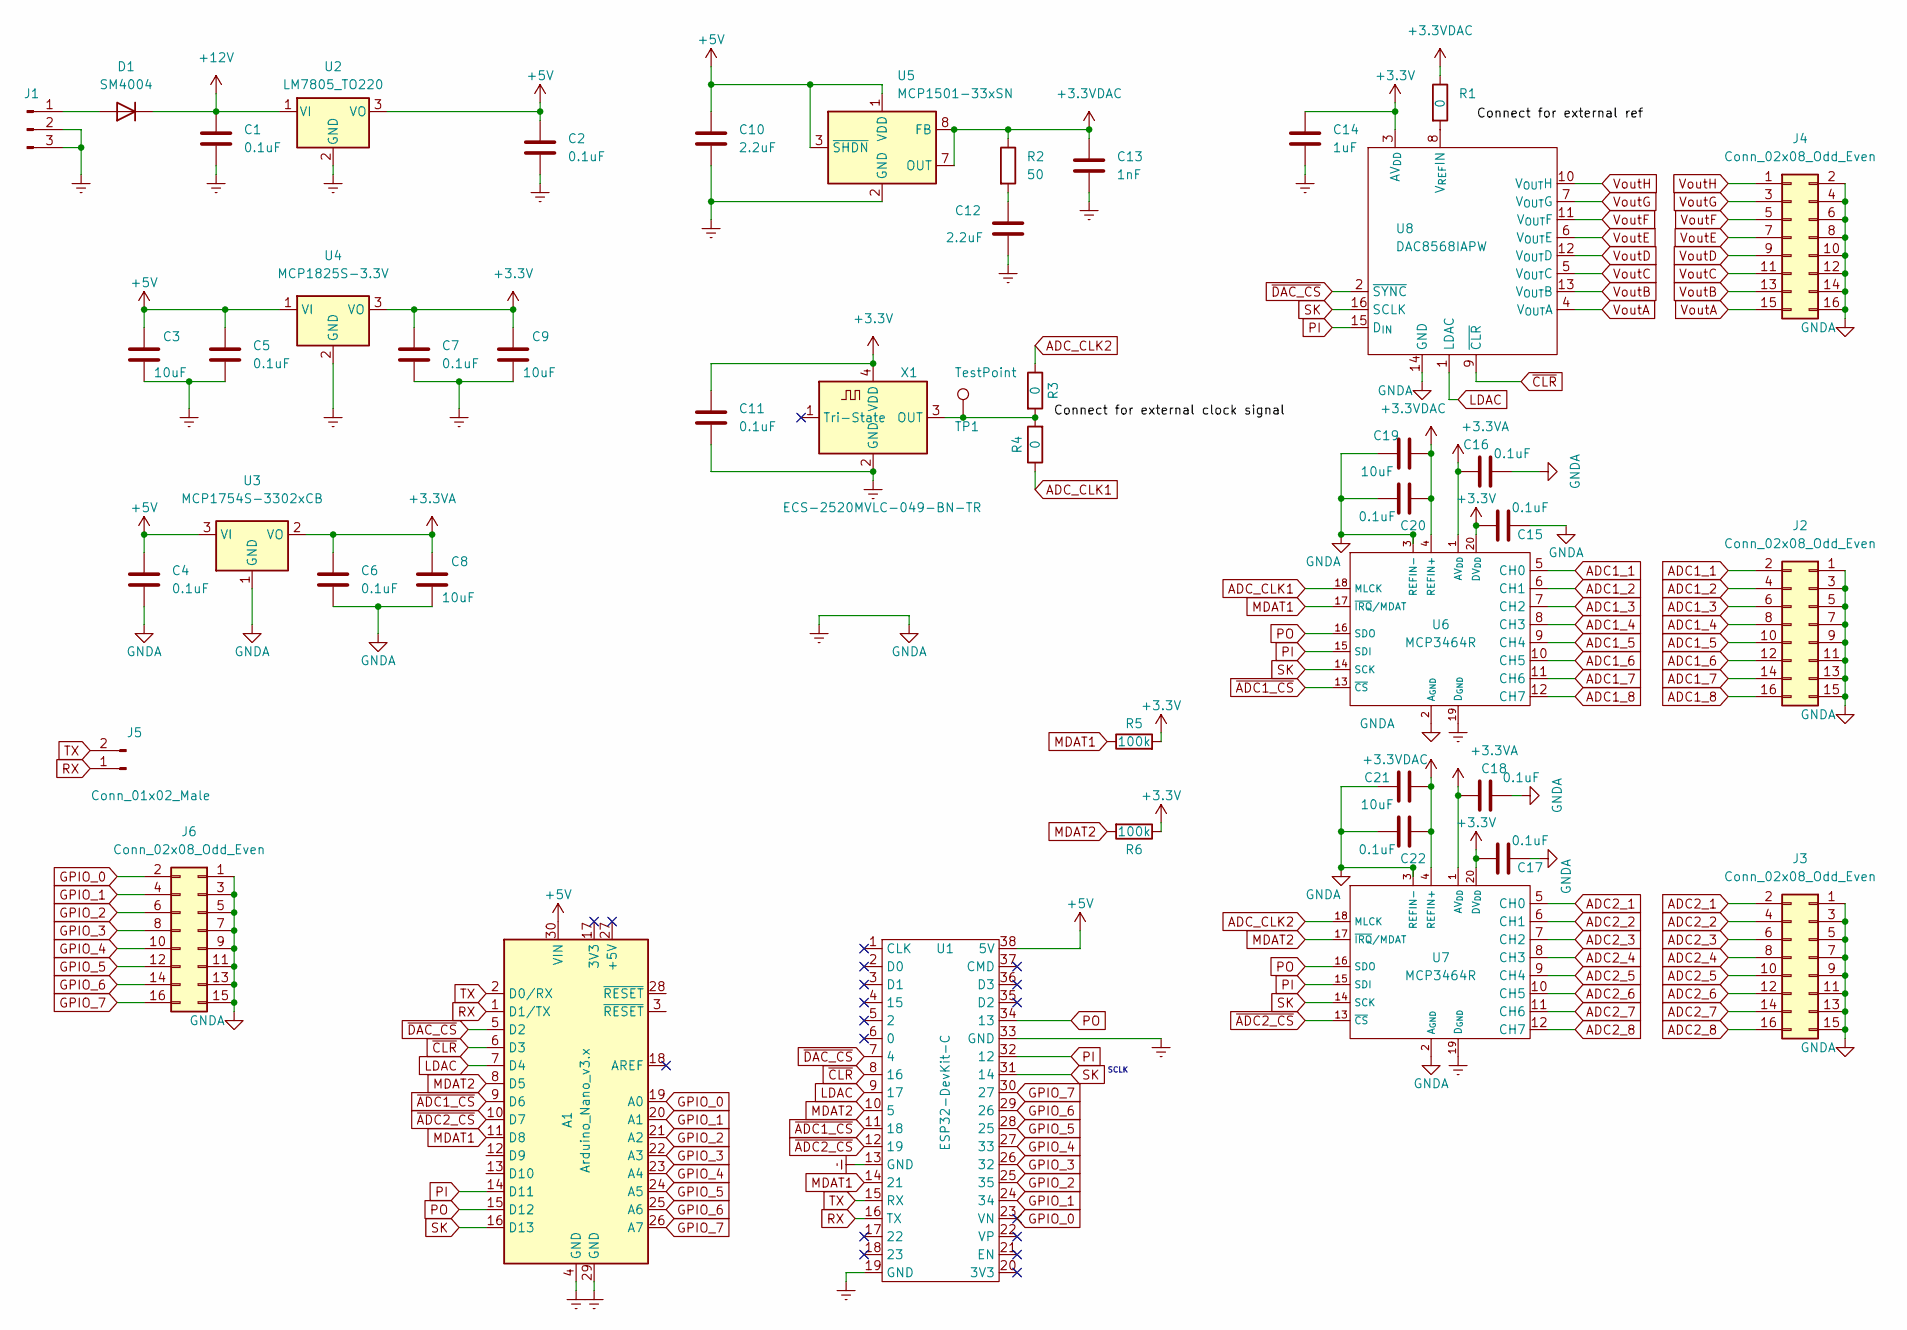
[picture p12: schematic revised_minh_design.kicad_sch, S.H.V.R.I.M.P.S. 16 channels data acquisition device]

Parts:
A1: Arduino_Nano_v3.x; Arduino_Nano
C1, C2, C4, C5, C6, C7, C11, C15, C16, C17, C18, C20, C22: 0.1uF; C_0805_2012Metric_Pad1.18x1.45mm_HandSolder
C3, C8, C9, C19, C21: 10uF; C_0805_2012Metric_Pad1.18x1.45mm_HandSolder
C10, C12: 2.2uF; C_0805_2012Metric_Pad1.18x1.45mm_HandSolder
C13: 1nF; C_0805_2012Metric_Pad1.18x1.45mm_HandSolder
C14: 1uF; C_0805_2012Metric_Pad1.18x1.45mm_HandSolder
D1: SM4004; D_MELF
J1: Conn_01x03_Male; PinSocket_1x03_P2.54mm_Vertical
J2, J3, J4, J6: Conn_02x08_Odd_Even; PinSocket_2x08_P2.54mm_Vertical
J5: Conn_01x02_Male; PinSocket_1x02_P2.54mm_Vertical
R1, R3, R4: 0; R_0805_2012Metric_Pad1.20x1.40mm_HandSolder
R2: 50; R_0805_2012Metric_Pad1.20x1.40mm_HandSolder
R5, R6: 100k; R_0805_2012Metric_Pad1.20x1.40mm_HandSolder
TP1: TestPoint; PinHeader_1x01_P2.54mm_Vertical
U1: ESP32-DevKit-C; ESP32-devkitC-v4
U2: LM7805_TO220; TO-220-3_Vertical
U3: MCP1754S-3302xCB; SOT-23
U4: MCP1825S-3.3V; SOT-223-3_TabPin2
U5: MCP1501-33xSN; SOIC-8_3.9x4.9mm_P1.27mm
U6, U7: MCP3464R; TSSOP-20_4.4x6.5mm_P0.65mm
U8: DAC8568IAPW; TSSOP-16-1EP_4.4x5mm_P0.65mm
X1: ECS-2520MVLC-049-BN-TR; Oscillator_SMD_ECS_2520MV-xxx-xx-4Pin_2.5x2.0mm

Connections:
+3.3VA: C6.1, C8.1, C16.1, C18.1, U3.2 (VO), U6.1 (AV_{DD}), U7.1 (AV_{DD})
+3.3VDAC: C13.1, C19.1, C20.1, C21.1, C22.1, R1.1, R2.1, U5.7 (OUT), U5.8 (FB), U6.4 (REFIN+), U7.4 (REFIN+)
+3V3: C7.1, C9.1, C11.1, C14.1, C15.1, C17.1, R5.2, R6.1, U4.3 (VO), U6.20 (DV_{DD}), U7.20 (DV_{DD}), U8.3 (AV_{DD}), X1.4 (VDD)
+5V: A1.30 (VIN), C2.1, C3.1, C4.1, C5.1, C10.1, U1.38 (5V), U2.3 (VO), U3.3 (VI), U4.1 (VI), U5.1 (VDD), U5.3 (~SHDN)
+12V: C1.1, D1.1 (K), U2.1 (VI)
ADC1_1: J2.2, U6.5 (CH0)
ADC1_2: J2.4, U6.6 (CH1)
ADC1_3: J2.6, U6.7 (CH2)
ADC1_4: J2.8, U6.8 (CH3)
ADC1_5: J2.10, U6.9 (CH4)
ADC1_6: J2.12, U6.10 (CH5)
ADC1_7: J2.14, U6.11 (CH6)
ADC1_8: J2.16, U6.12 (CH7)
ADC2_1: J3.2, U7.5 (CH0)
ADC2_2: J3.4, U7.6 (CH1)
ADC2_3: J3.6, U7.7 (CH2)
ADC2_4: J3.8, U7.8 (CH3)
ADC2_5: J3.10, U7.9 (CH4)
ADC2_6: J3.12, U7.10 (CH5)
ADC2_7: J3.14, U7.11 (CH6)
ADC2_8: J3.16, U7.12 (CH7)
ADC_CLK1: R4.1, U6.18 (MLCK)
ADC_CLK2: R3.1, U7.18 (MLCK)
Earth: A1.4 (GND), A1.29 (GND), C1.2, C2.2, C3.2, C4.2, C5.2, C6.2, C7.2, C8.2, C9.2, C10.2, C11.2, C12.2, C13.2, C14.2, C15.2, C16.2, C17.2, C18.2, C19.2, C20.2, C21.2, C22.2, J1.2, J1.3, J2.1, J2.3, J2.5, J2.7, J2.9, J2.11, J2.13, J2.15, J3.1, J3.3, J3.5, J3.7, J3.9, J3.11, J3.13, J3.15, J4.2, J4.4, J4.6, J4.8, J4.10, J4.12, J4.14, J4.16, J6.1, J6.3, J6.5, J6.7, J6.9, J6.11, J6.13, J6.15, U1.13 (GND), U1.19 (GND), U1.33 (GND), U2.2 (GND), U3.1 (GND), U4.2 (GND), U5.2 (GND), U5.4 (GND), U5.5 (GND), U5.6 (GND), U6.2 (A_{GND}), U6.3 (REFIN-), U6.19 (D_{GND}), U7.2 (A_{GND}), U7.3 (REFIN-), U7.19 (D_{GND}), U8.14 (GND), X1.2 (GND)
GPIO_0: A1.19 (A0), J6.2, U1.23 (VN)
GPIO_1: A1.20 (A1), J6.4, U1.24 (34)
GPIO_2: A1.21 (A2), J6.6, U1.25 (35)
GPIO_3: A1.22 (A3), J6.8, U1.26 (32)
GPIO_4: A1.23 (A4), J6.10, U1.27 (33)
GPIO_5: A1.24 (A5), J6.12, U1.28 (25)
GPIO_6: A1.25 (A6), J6.14, U1.29 (26)
GPIO_7: A1.26 (A7), J6.16, U1.30 (27)
LDAC: A1.7 (D4), U1.9 (17), U8.1 (LDAC)
MDAT1: A1.11 (D8), R5.1, U1.14 (21), U6.17 (~IRQ/MDAT)
MDAT2: A1.8 (D5), R6.2, U1.10 (5), U7.17 (~IRQ/MDAT)
unnamed: C12.1, R2.2
unnamed: D1.2 (A), J1.1
unnamed: R1.2, U8.8 (V_{REF}IN)
unnamed: R3.2, R4.2, TP1.1, X1.3 (OUT)
PI: A1.14 (D11), U1.32 (12), U6.15 (SDI), U7.15 (SDI), U8.15 (D_{IN})
PO: A1.15 (D12), U1.34 (13), U6.16 (SDO), U7.16 (SDO)
RX: A1.1 (D1/TX), J5.1, U1.16 (TX)
SK: A1.16 (D13), U1.31 (14), U6.14 (SCK), U7.14 (SCK), U8.16 (SCLK)
TX: A1.2 (D0/RX), J5.2, U1.15 (RX)
VoutA: J4.15, U8.4 (V_{OUT}A)
VoutB: J4.13, U8.13 (V_{OUT}B)
VoutC: J4.11, U8.5 (V_{OUT}C)
VoutD: J4.9, U8.12 (V_{OUT}D)
VoutE: J4.7, U8.6 (V_{OUT}E)
VoutF: J4.5, U8.11 (V_{OUT}F)
VoutG: J4.3, U8.7 (V_{OUT}G)
VoutH: J4.1, U8.10 (V_{OUT}H)
~ADC1_CS: A1.9 (D6), U1.11 (18), U6.13 (~CS)
~ADC2_CS: A1.10 (D7), U1.12 (19), U7.13 (~CS)
~CLR: A1.6 (D3), U1.8 (16), U8.9 (~CLR)
~DAC_CS: A1.5 (D2), U1.7 (4), U8.2 (~SYNC)

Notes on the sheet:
SCLK

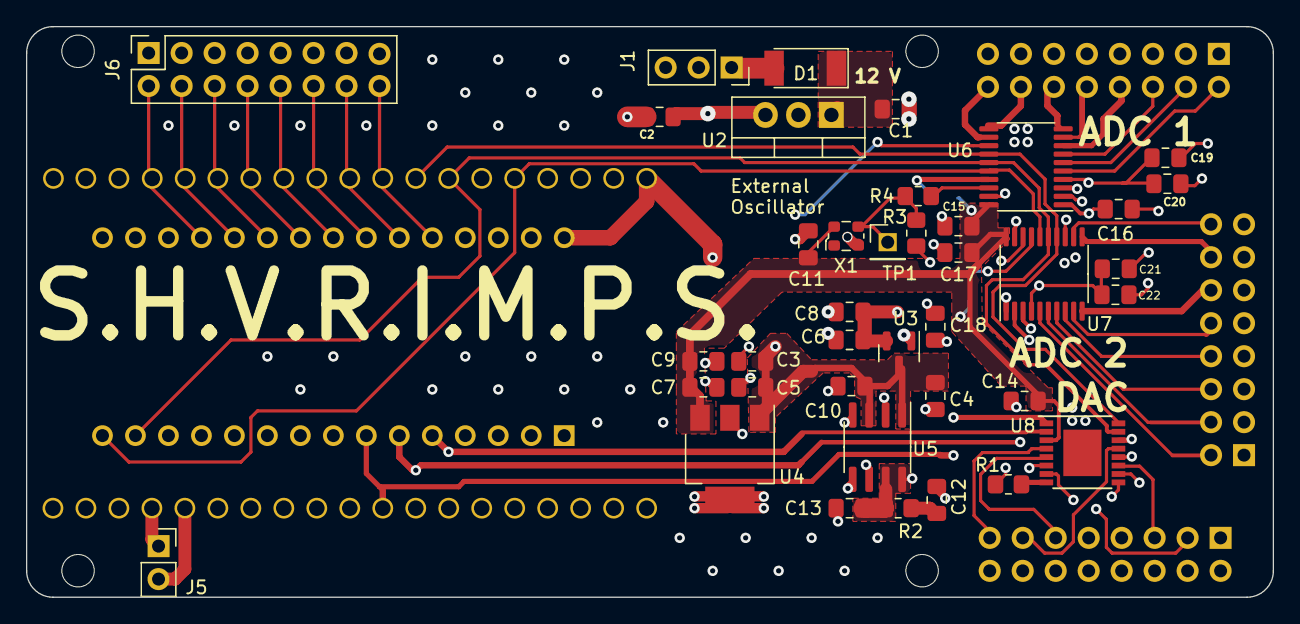
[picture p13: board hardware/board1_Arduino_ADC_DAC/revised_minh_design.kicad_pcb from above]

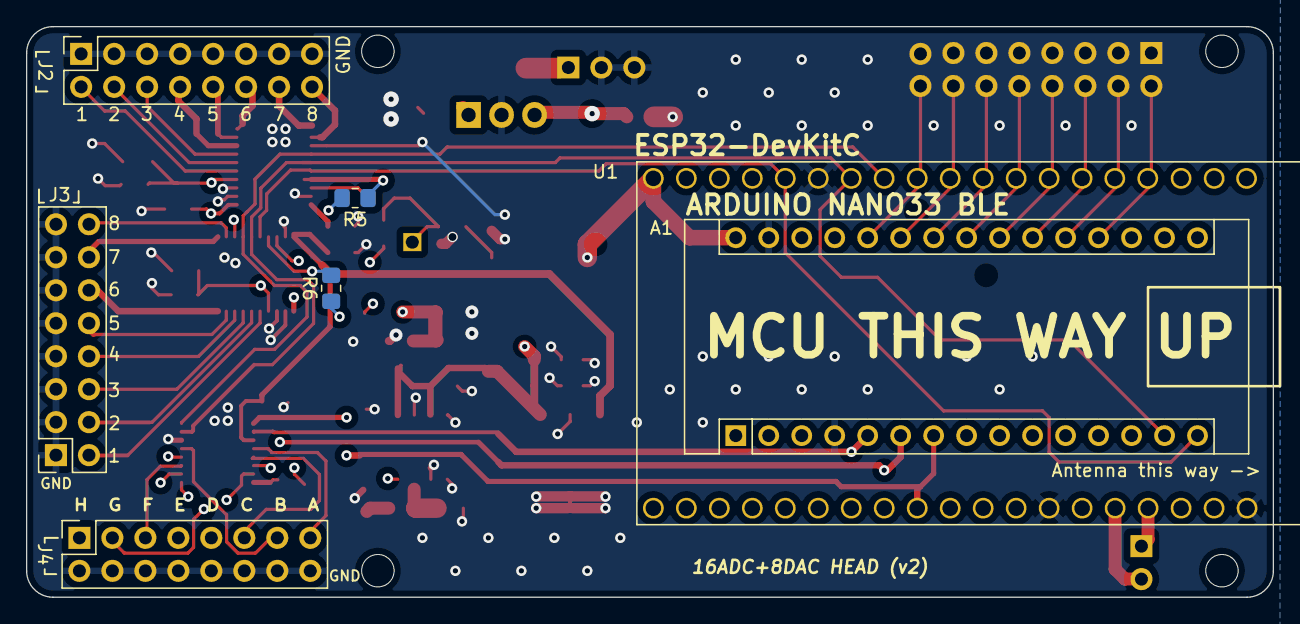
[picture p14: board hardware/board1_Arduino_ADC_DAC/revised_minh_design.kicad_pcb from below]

Board: 4 copper layers, 96.0 x 43.9 mm, 50 parts (7 on the bottom side), 56 nets.

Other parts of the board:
 : MountingHole_2.5mm
 #2,  #3,  #4: MountingHole_2.5mm

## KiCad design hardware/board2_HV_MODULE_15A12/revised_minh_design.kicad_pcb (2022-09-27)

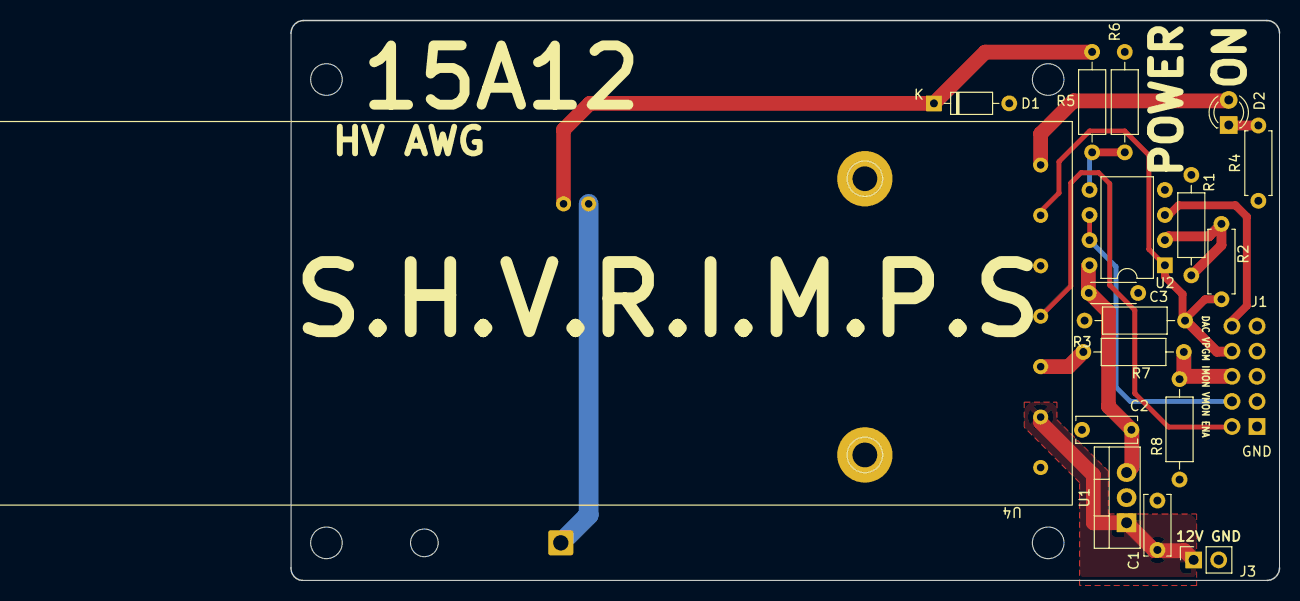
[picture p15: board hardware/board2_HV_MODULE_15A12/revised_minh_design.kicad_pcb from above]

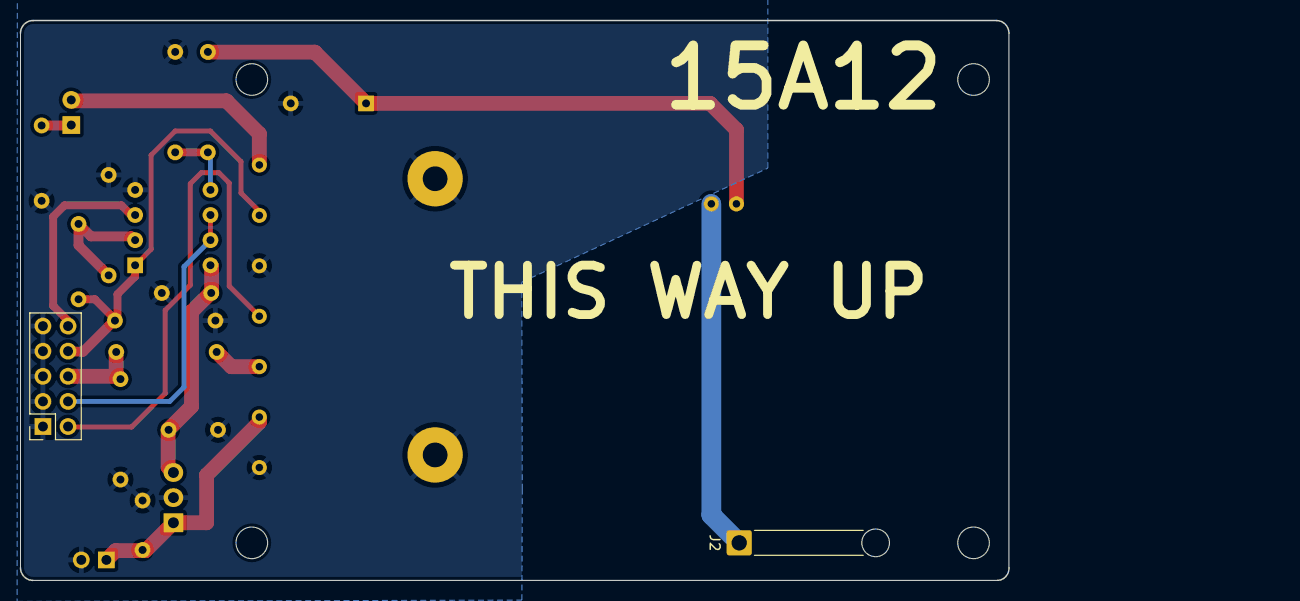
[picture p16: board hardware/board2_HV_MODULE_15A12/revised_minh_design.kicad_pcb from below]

Board: 2 copper layers, 100.0 x 56.6 mm, 25 parts (2 on the bottom side), 15 nets.

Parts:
 : MountingHole_3.2mm_M3
 #2,  #4,  #6: MountingHole_3.2mm_M3
 #3: MountingHole_3.2mm_M3_DIN965_Pad
 #5: (no value)
C1, C2: 0.1uF; C_Disc_D6.0mm_W2.5mm_P5.00mm
C3: 0.1uF; C_Disc_D4.3mm_W1.9mm_P5.00mm
D1: TZX3V6A-TR; D_DO-35_SOD27_P7.62mm_Horizontal
D2: LED; LED_D3.0mm_Clear
J1: Conn_01x07_Male; PinSocket_2x05_P2.54mm_Vertical
J2: Conn_01x01_Male; SolderWire-0.75sqmm_1x01_D1.25mm_OD2.3mm_Relief
J3: Conn_01x02_Male; PinSocket_1x02_P2.54mm_Vertical
R1: 4.7k; R_Axial_DIN0207_L6.3mm_D2.5mm_P10.16mm_Horizontal
R2: 2k; R_Axial_DIN0207_L6.3mm_D2.5mm_P7.62mm_Horizontal
R3: 10k; R_Axial_DIN0207_L6.3mm_D2.5mm_P10.16mm_Horizontal
R4: 2.2k; R_Axial_DIN0207_L6.3mm_D2.5mm_P7.62mm_Horizontal
R5, R7: 3k9; R_Axial_DIN0207_L6.3mm_D2.5mm_P10.16mm_Horizontal
R6, R8: 1k1; R_Axial_DIN0207_L6.3mm_D2.5mm_P10.16mm_Horizontal
U1: LM7805_TO220; TO-220-3_Vertical
U2: NE5532; DIP-8_W7.62mm
U4: 15A12; Advanced Energy 15A12P4

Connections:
+5V: C2.1, C3.1, U1.3 (VO), U2.8 (V+)
+12V: C1.1, J3.1, U1.1 (VI), U4.2 (DC_INPUT_POWER)
DAC_SIG: J1.10, U2.3 (+)
ENABLE: J1.2, U4.4 (HV_ENABLE)
IMON: R7.2, U4.3 (Imon)
IMON_3V3: J1.6, R7.1, R8.2
unnamed: D2.1 (K), R4.2
unnamed: D2.2 (A), U4.7 (5VDC_REF)
unnamed: J2.1, U4.2-1 (HV_RTN)
unnamed: R1.1, R2.1, U2.2 (-)
SGND: #3.1, #5.1, C1.2, C2.2, C3.2, D1.2 (A), J1.1, J1.3, J1.5, J1.7, J1.9, J3.2, R1.2, R3.2, R4.1, R6.1, R8.1, U1.2 (GND), U2.4 (V-), U4.1 (DC_INPUT_POWER_GROUND), U4.5 (SIGNAL_GROUND_RET)
VMON: D1.1 (K), R5.2, U4.2-2 (Vmon)
VMON_3V3: J1.4, U2.6 (-), U2.7
VMON_OPAMP: R5.1, R6.2, U2.5 (+)
VPGM: J1.8, R2.2, R3.1, U2.1, U4.6 (Vprog)

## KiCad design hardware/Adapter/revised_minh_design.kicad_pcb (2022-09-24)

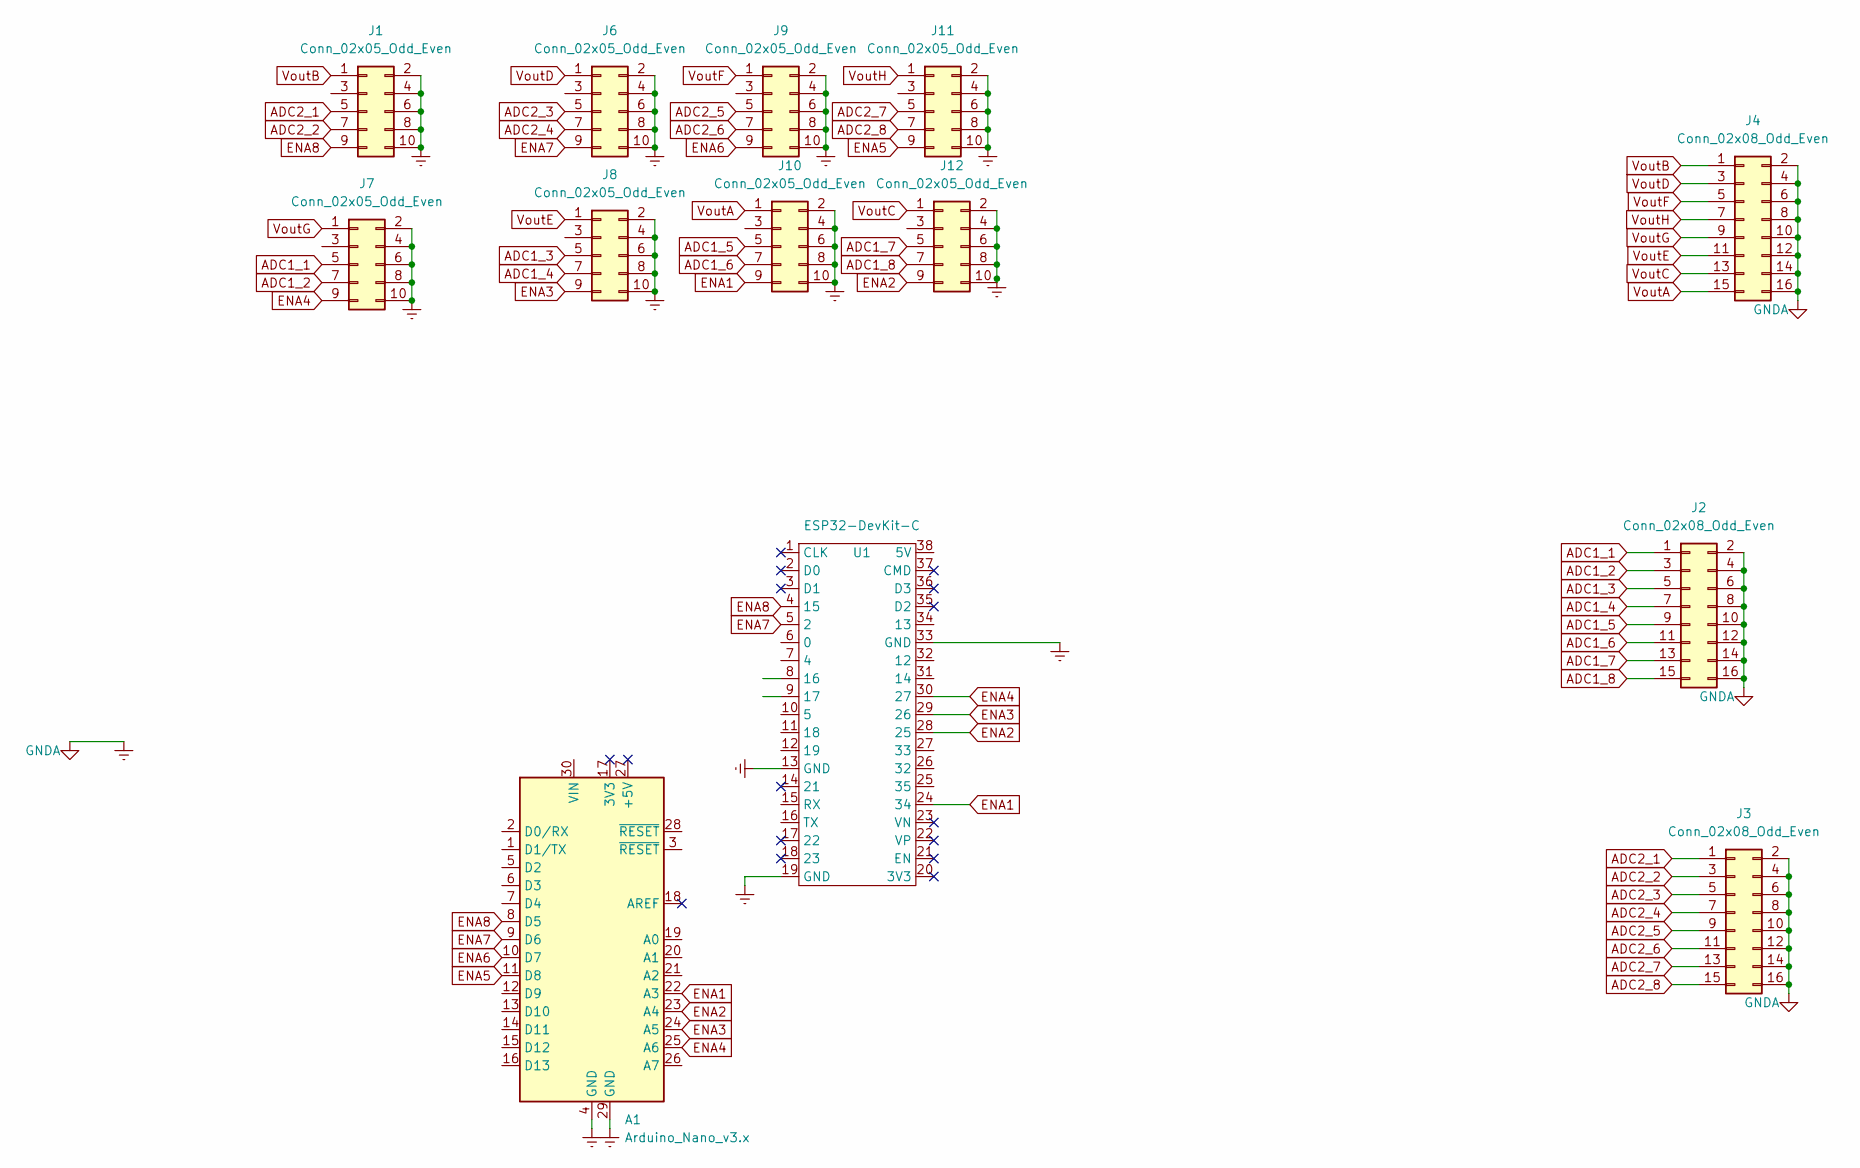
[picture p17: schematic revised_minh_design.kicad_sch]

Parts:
A1: Arduino_Nano_v3.x; Arduino_Nano
J1, J6, J7, J8, J9, J10, J11, J12: Conn_02x05_Odd_Even; PinSocket_2x05_P2.54mm_Vertical
J2, J3, J4: Conn_02x08_Odd_Even; PinSocket_2x08_P2.54mm_Vertical
U1: ESP32-DevKit-C; ESP32-devkitC-v4

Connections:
ADC1_1: J2.1, J7.5
ADC1_2: J2.3, J7.7
ADC1_3: J2.5, J8.5
ADC1_4: J2.7, J8.7
ADC1_5: J2.9, J10.5
ADC1_6: J2.11, J10.7
ADC1_7: J2.13, J12.5
ADC1_8: J2.15, J12.7
ADC2_1: J1.5, J3.1
ADC2_2: J1.7, J3.3
ADC2_3: J3.5, J6.5
ADC2_4: J3.7, J6.7
ADC2_5: J3.9, J9.5
ADC2_6: J3.11, J9.7
ADC2_7: J3.13, J11.5
ADC2_8: J3.15, J11.7
ENA1: A1.22 (A3), J10.9, U1.24 (34)
ENA2: A1.23 (A4), J12.9, U1.28 (25)
ENA3: A1.24 (A5), J8.9, U1.29 (26)
ENA4: A1.25 (A6), J7.9, U1.30 (27)
ENA5: A1.11 (D8), J11.9
ENA6: A1.10 (D7), J9.9
ENA7: A1.9 (D6), J6.9, U1.5 (2)
ENA8: A1.8 (D5), J1.9, U1.4 (15)
Earth: A1.4 (GND), A1.29 (GND), J1.2, J1.4, J1.6, J1.8, J1.10, J2.2, J2.4, J2.6, J2.8, J2.10, J2.12, J2.14, J2.16, J3.2, J3.4, J3.6, J3.8, J3.10, J3.12, J3.14, J3.16, J4.2, J4.4, J4.6, J4.8, J4.10, J4.12, J4.14, J4.16, J6.2, J6.4, J6.6, J6.8, J6.10, J7.2, J7.4, J7.6, J7.8, J7.10, J8.2, J8.4, J8.6, J8.8, J8.10, J9.2, J9.4, J9.6, J9.8, J9.10, J10.2, J10.4, J10.6, J10.8, J10.10, J11.2, J11.4, J11.6, J11.8, J11.10, J12.2, J12.4, J12.6, J12.8, J12.10, U1.13 (GND), U1.19 (GND), U1.33 (GND)
VoutA: J4.15, J10.1
VoutB: J1.1, J4.1
VoutC: J4.13, J12.1
VoutD: J4.3, J6.1
VoutE: J4.11, J8.1
VoutF: J4.5, J9.1
VoutG: J4.9, J7.1
VoutH: J4.7, J11.1

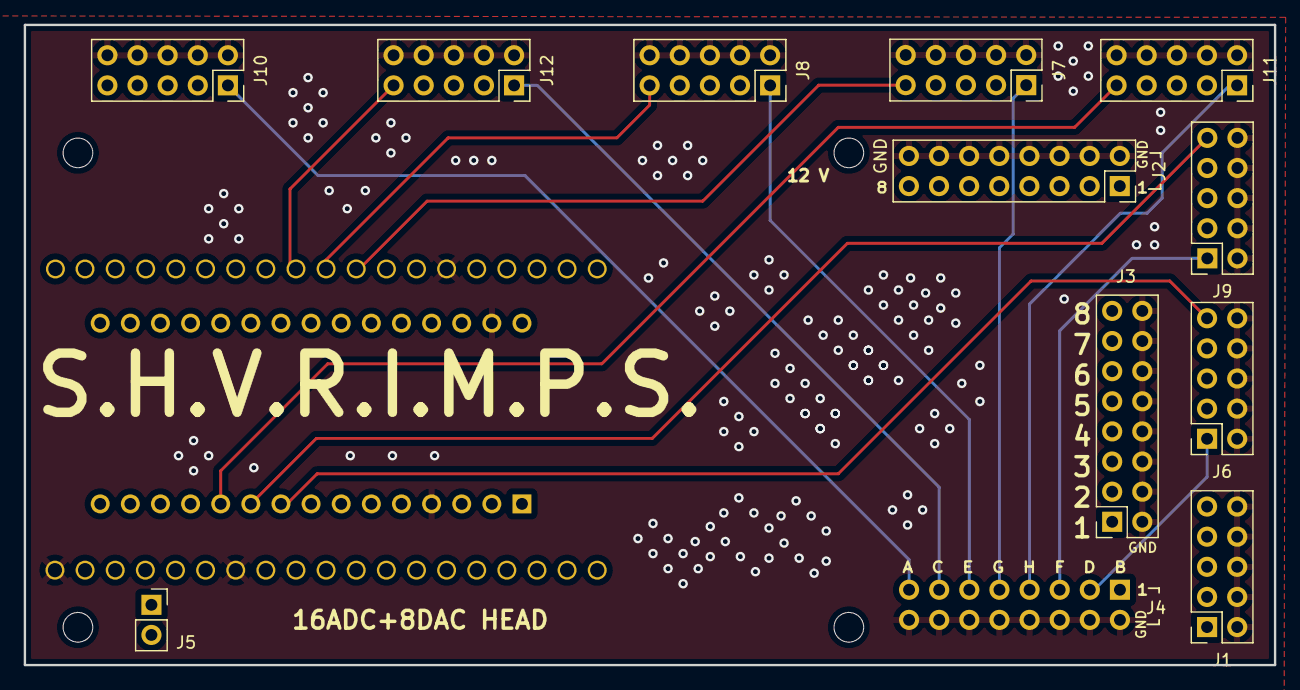
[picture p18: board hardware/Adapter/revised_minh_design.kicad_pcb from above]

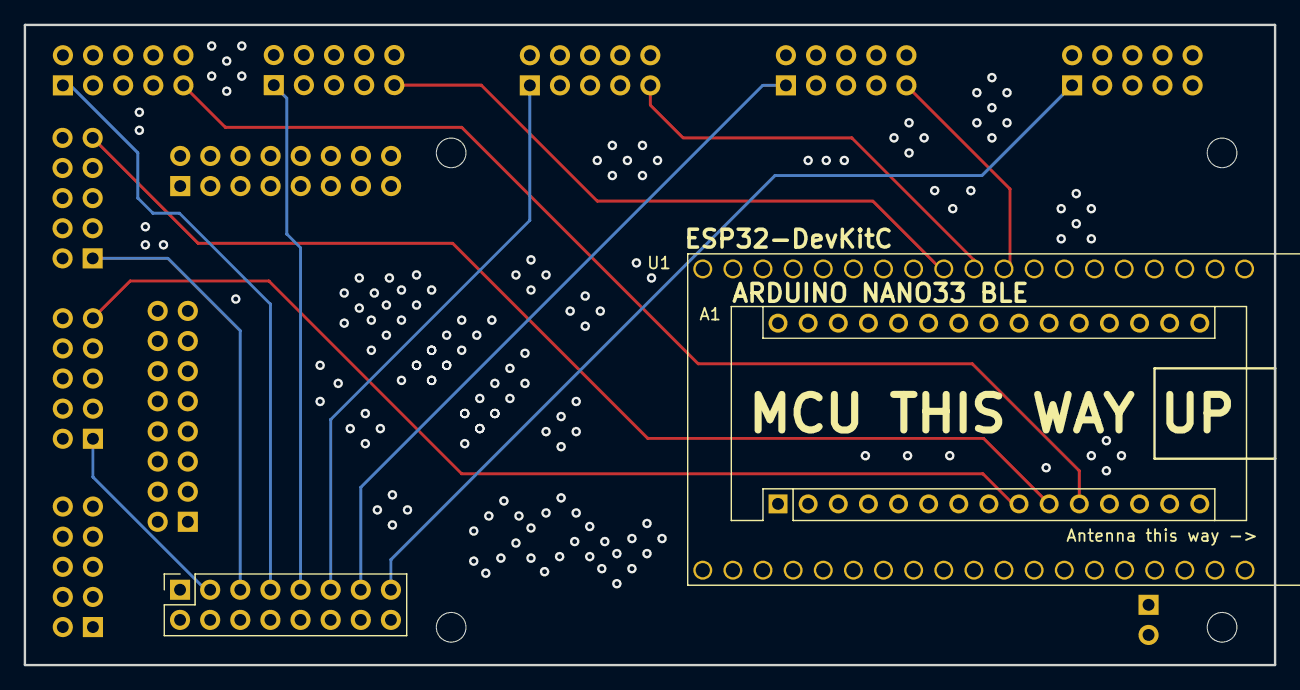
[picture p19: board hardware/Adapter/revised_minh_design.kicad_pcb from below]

Board: 4 copper layers, 105.4 x 54.0 mm, 18 parts (3 on the bottom side), 33 nets.

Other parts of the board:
 : MountingHole_2.5mm
 #2,  #3,  #4: MountingHole_2.5mm
J5: Conn_01x02_Male; PinSocket_1x02_P2.54mm_Vertical

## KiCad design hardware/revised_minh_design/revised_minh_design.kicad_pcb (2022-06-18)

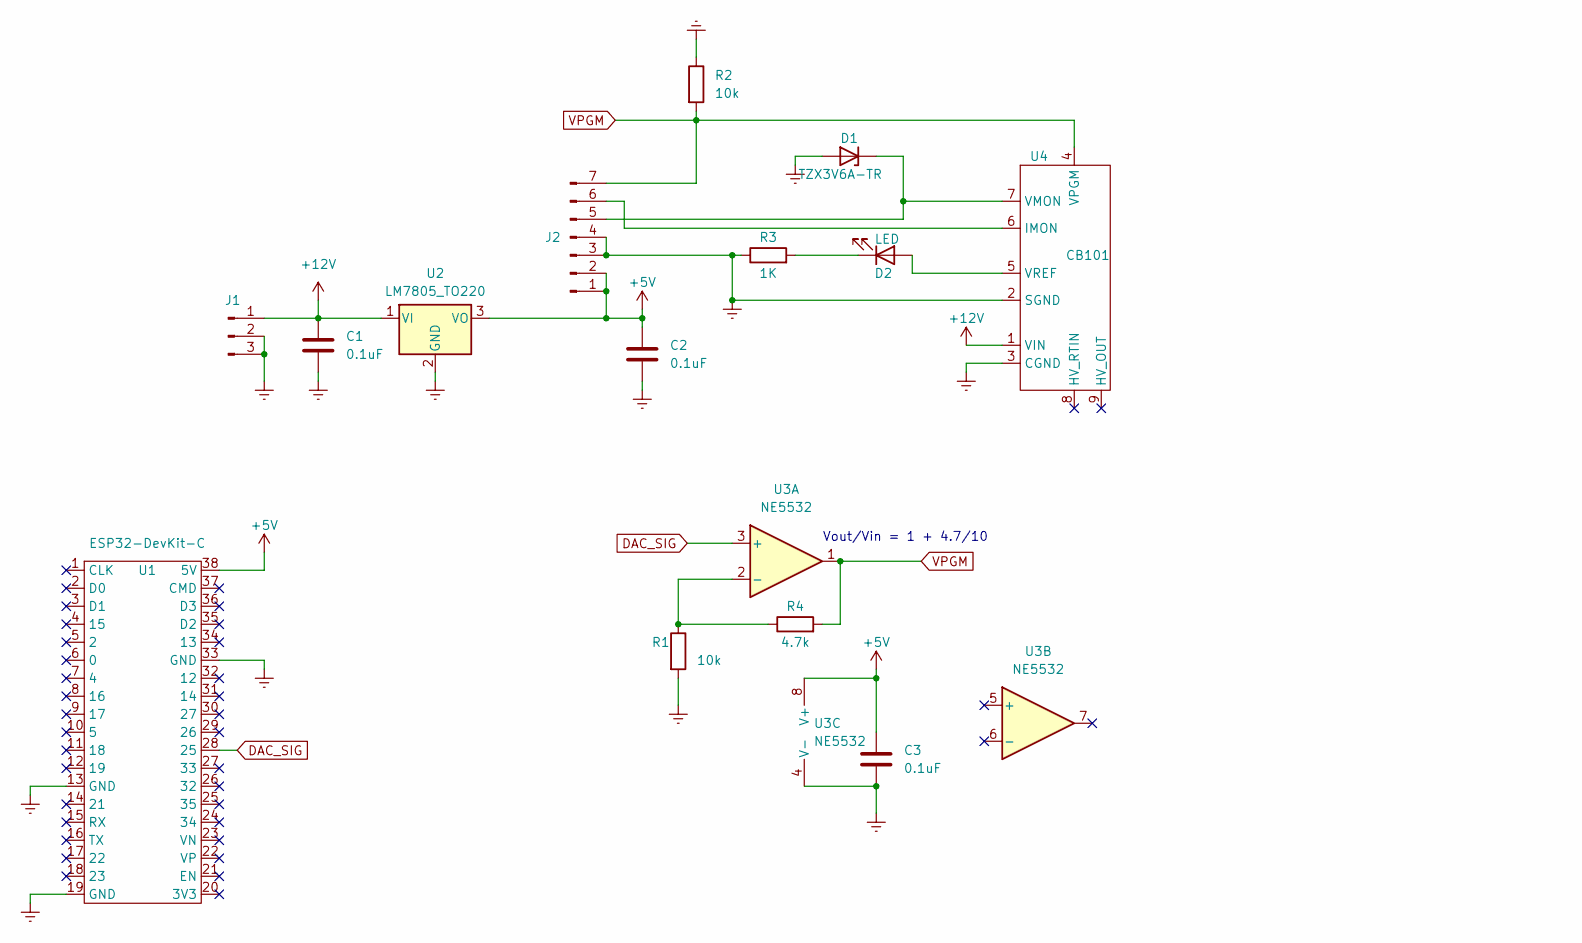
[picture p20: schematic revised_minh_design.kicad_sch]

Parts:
C1, C2, C3: 0.1uF; C_Disc_D6.0mm_W2.5mm_P5.00mm
D1: TZX3V6A-TR; D_DO-35_SOD27_P7.62mm_Horizontal
D2: LED; LED_D3.0mm_Clear
J1: Conn_01x03_Male; PinSocket_1x03_P2.54mm_Vertical
J2: Conn_01x07_Male; PinSocket_1x07_P2.54mm_Vertical
R1, R2: 10k; R_Axial_DIN0309_L9.0mm_D3.2mm_P15.24mm_Horizontal
R3: 1K; R_Axial_DIN0309_L9.0mm_D3.2mm_P15.24mm_Horizontal
R4: 4.7k; R_Axial_DIN0309_L9.0mm_D3.2mm_P15.24mm_Horizontal
U1: ESP32-DevKit-C; ESP32-devkitC-v4
U2: LM7805_TO220; TO-220-3_Vertical
U3: NE5532; DIP-8_W7.62mm
U4: CB101

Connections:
+5V: C2.1, C3.1, J2.1, J2.2, U1.38 (5V), U2.3 (VO), U3.8 (V+)
+12V: C1.1, J1.1, U2.1 (VI), U4.1 (VIN)
DAC_SIG: U1.28 (25), U3.3 (+)
Earth: C1.2, C2.2, C3.2, D1.2 (A), J1.2, J1.3, J2.3, J2.4, R1.2, R2.1, R3.1, U1.13 (GND), U1.19 (GND), U1.33 (GND), U2.2 (GND), U3.4 (V-), U4.2 (SGND), U4.3 (CGND)
unnamed: D1.1 (K), J2.5, U4.7 (VMON)
unnamed: D2.1 (K), R3.2
unnamed: D2.2 (A), U4.5 (VREF)
unnamed: J2.6, U4.6 (IMON)
unnamed: R1.1, R4.1, U3.2 (-)
VPGM: J2.7, R2.2, R4.2, U3.1, U4.4 (VPGM)

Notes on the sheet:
Vout/Vin = 1 + 4.7/10

Board: 2 copper layers, 15 parts (0 on the bottom side), 10 nets, no tracks yet.

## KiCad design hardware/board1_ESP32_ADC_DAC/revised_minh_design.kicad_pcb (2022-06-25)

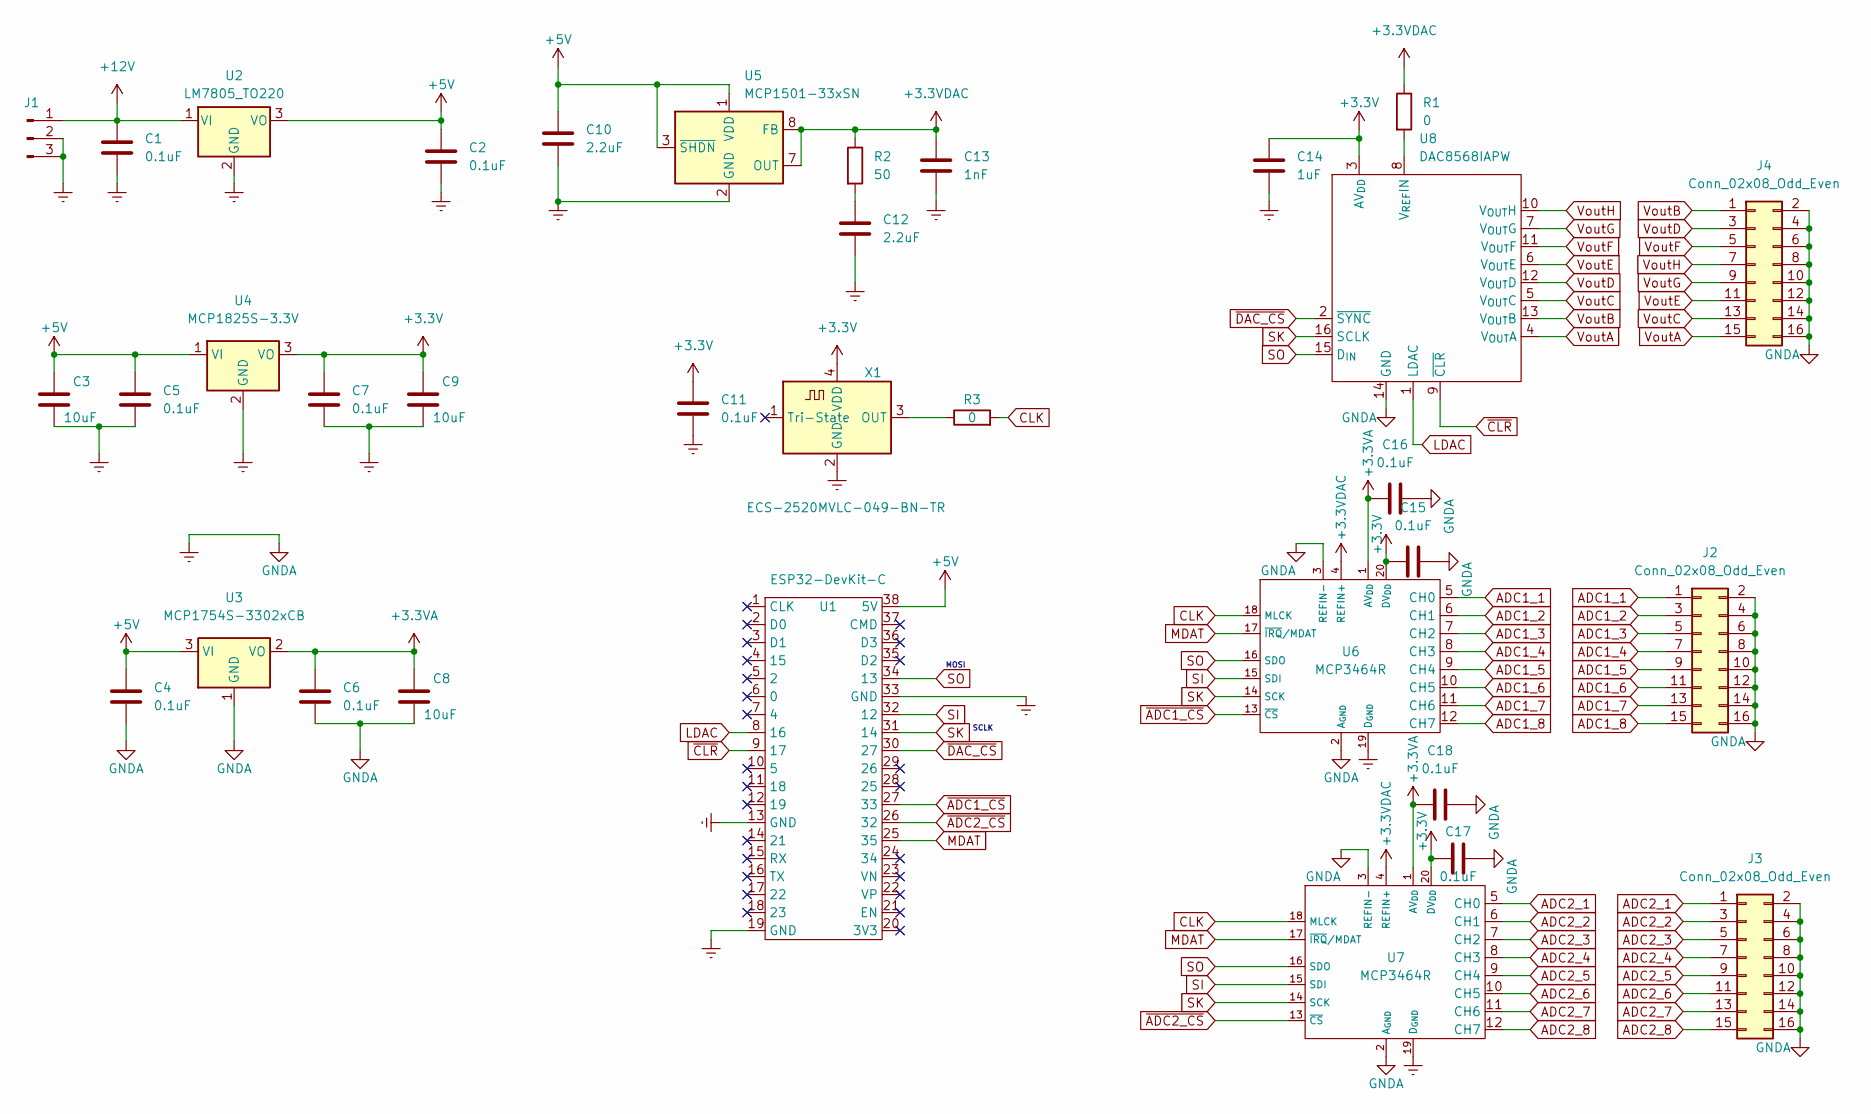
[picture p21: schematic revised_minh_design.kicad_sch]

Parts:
C1, C2, C4, C5, C6, C7, C11, C15, C16, C17, C18: 0.1uF; C_0805_2012Metric_Pad1.18x1.45mm_HandSolder
C3, C8, C9: 10uF; C_0805_2012Metric_Pad1.18x1.45mm_HandSolder
C10, C12: 2.2uF; C_0805_2012Metric_Pad1.18x1.45mm_HandSolder
C13: 1nF; C_0805_2012Metric_Pad1.18x1.45mm_HandSolder
C14: 1uF; C_0805_2012Metric_Pad1.18x1.45mm_HandSolder
J1: Conn_01x03_Male; PinSocket_1x03_P2.54mm_Vertical
J2, J3, J4: Conn_02x08_Odd_Even; PinSocket_2x08_P2.54mm_Vertical
R1, R3: 0; R_0805_2012Metric_Pad1.20x1.40mm_HandSolder
R2: 50; R_0805_2012Metric_Pad1.20x1.40mm_HandSolder
U1: ESP32-DevKit-C; ESP32-devkitC-v4
U2: LM7805_TO220; TO-220-3_Vertical
U3: MCP1754S-3302xCB; SOT-23
U4: MCP1825S-3.3V; SOT-223-3_TabPin2
U5: MCP1501-33xSN; SOIC-8_3.9x4.9mm_P1.27mm
U6, U7: MCP3464R; TSSOP-20_4.4x6.5mm_P0.65mm
U8: DAC8568IAPW; TSSOP-16-1EP_4.4x5mm_P0.65mm
X1: ECS-2520MVLC-049-BN-TR; Oscillator_SMD_ECS_2520MV-xxx-xx-4Pin_2.5x2.0mm

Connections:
+3.3VA: C6.1, C8.1, C16.1, C18.1, U3.2 (VO), U6.1 (AV_{DD}), U7.1 (AV_{DD})
+3.3VDAC: C13.1, R1.1, R2.1, U5.7 (OUT), U5.8 (FB), U6.4 (REFIN+), U7.4 (REFIN+)
+3V3: C7.1, C9.1, C11.1, C14.1, C15.1, C17.1, U4.3 (VO), U6.20 (DV_{DD}), U7.20 (DV_{DD}), U8.3 (AV_{DD}), X1.4 (VDD)
+5V: C2.1, C3.1, C4.1, C5.1, C10.1, U1.38 (5V), U2.3 (VO), U3.3 (VI), U4.1 (VI), U5.1 (VDD), U5.3 (~SHDN)
+12V: C1.1, J1.1, U2.1 (VI)
ADC1_1: J2.1, U6.5 (CH0)
ADC1_2: J2.3, U6.6 (CH1)
ADC1_3: J2.5, U6.7 (CH2)
ADC1_4: J2.7, U6.8 (CH3)
ADC1_5: J2.9, U6.9 (CH4)
ADC1_6: J2.11, U6.10 (CH5)
ADC1_7: J2.13, U6.11 (CH6)
ADC1_8: J2.15, U6.12 (CH7)
ADC2_1: J3.1, U7.5 (CH0)
ADC2_2: J3.3, U7.6 (CH1)
ADC2_3: J3.5, U7.7 (CH2)
ADC2_4: J3.7, U7.8 (CH3)
ADC2_5: J3.9, U7.9 (CH4)
ADC2_6: J3.11, U7.10 (CH5)
ADC2_7: J3.13, U7.11 (CH6)
ADC2_8: J3.15, U7.12 (CH7)
CLK: R3.2, U6.18 (MLCK), U7.18 (MLCK)
Earth: C1.2, C2.2, C3.2, C4.2, C5.2, C6.2, C7.2, C8.2, C9.2, C10.2, C11.2, C12.2, C13.2, C14.2, C15.2, C16.2, C17.2, C18.2, J1.2, J1.3, J2.2, J2.4, J2.6, J2.8, J2.10, J2.12, J2.14, J2.16, J3.2, J3.4, J3.6, J3.8, J3.10, J3.12, J3.14, J3.16, J4.2, J4.4, J4.6, J4.8, J4.10, J4.12, J4.14, J4.16, U1.13 (GND), U1.19 (GND), U1.33 (GND), U2.2 (GND), U3.1 (GND), U4.2 (GND), U5.2 (GND), U5.4 (GND), U5.5 (GND), U5.6 (GND), U6.2 (A_{GND}), U6.3 (REFIN-), U6.19 (D_{GND}), U7.2 (A_{GND}), U7.3 (REFIN-), U7.19 (D_{GND}), U8.14 (GND), X1.2 (GND)
LDAC: U1.8 (16), U8.1 (LDAC)
MDAT: U1.25 (35), U6.17 (~IRQ/MDAT), U7.17 (~IRQ/MDAT)
unnamed: C12.1, R2.2
unnamed: R1.2, U8.8 (V_{REF}IN)
unnamed: R3.1, X1.3 (OUT)
SI: U1.32 (12), U6.15 (SDI), U7.15 (SDI)
SK: U1.31 (14), U6.14 (SCK), U7.14 (SCK), U8.16 (SCLK)
SO: U1.34 (13), U6.16 (SDO), U7.16 (SDO), U8.15 (D_{IN})
VoutA: J4.15, U8.4 (V_{OUT}A)
VoutB: J4.1, U8.13 (V_{OUT}B)
VoutC: J4.13, U8.5 (V_{OUT}C)
VoutD: J4.3, U8.12 (V_{OUT}D)
VoutE: J4.11, U8.6 (V_{OUT}E)
VoutF: J4.5, U8.11 (V_{OUT}F)
VoutG: J4.9, U8.7 (V_{OUT}G)
VoutH: J4.7, U8.10 (V_{OUT}H)
~ADC1_CS: U1.27 (33), U6.13 (~CS)
~ADC2_CS: U1.26 (32), U7.13 (~CS)
~CLR: U1.9 (17), U8.9 (~CLR)
~DAC_CS: U1.30 (27), U8.2 (~SYNC)

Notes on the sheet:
SCLK
MOSI

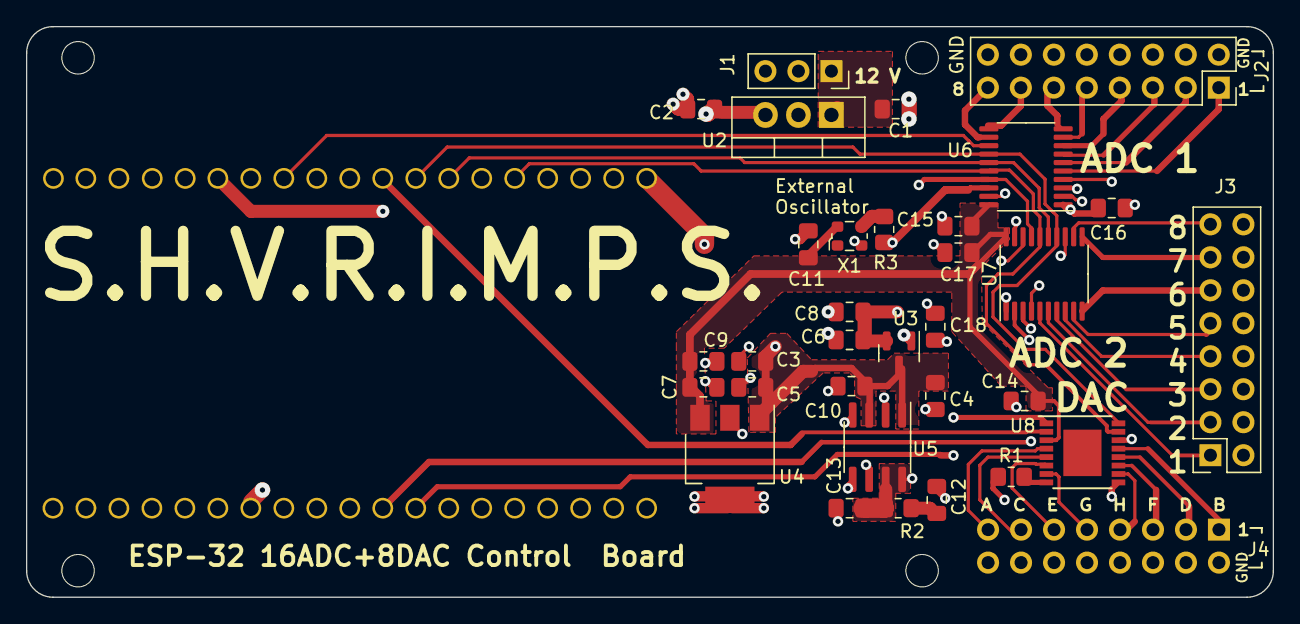
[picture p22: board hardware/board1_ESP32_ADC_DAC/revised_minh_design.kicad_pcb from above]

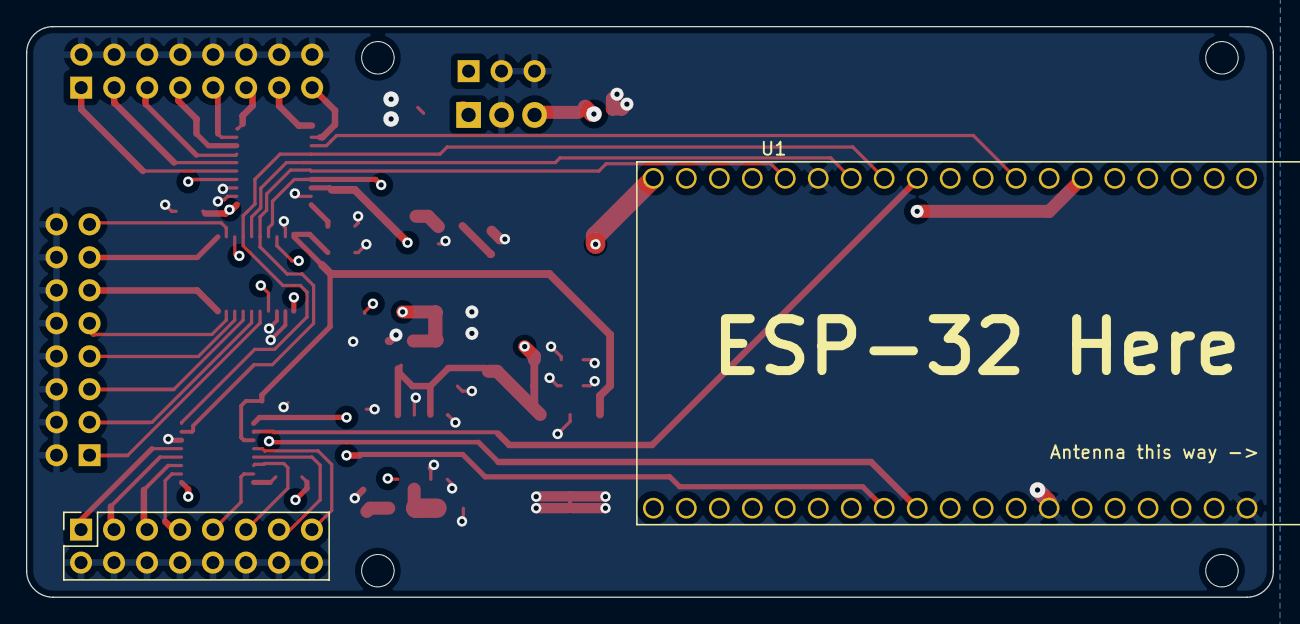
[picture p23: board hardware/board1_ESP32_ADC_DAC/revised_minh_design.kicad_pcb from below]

Board: 4 copper layers, 96.0 x 43.9 mm, 38 parts (2 on the bottom side), 43 nets.

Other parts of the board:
 : MountingHole_2.5mm
 #2,  #3,  #4: MountingHole_2.5mm

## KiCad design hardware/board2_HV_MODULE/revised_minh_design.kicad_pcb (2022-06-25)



Board: 2 copper layers, 100.3 x 42.3 mm, 20 parts (2 on the bottom side), 13 nets.

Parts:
 : MountingHole_2.5mm
 #2: MountingHole_2.5mm
C1, C2, C3: 0.1uF; C_Disc_D6.0mm_W2.5mm_P5.00mm
D1: TZX3V6A-TR; D_DO-35_SOD27_P7.62mm_Horizontal
D2: LED; LED_D3.0mm_Clear
J1: Conn_01x07_Male; PinSocket_1x07_P2.54mm_Vertical
J2: Conn_01x01_Male; SolderWire-0.75sqmm_1x01_D1.25mm_OD2.3mm_Relief
R1, R3: 10k; R_Axial_DIN0207_L6.3mm_D2.5mm_P10.16mm_Horizontal
R2: 4.7k; R_Axial_DIN0207_L6.3mm_D2.5mm_P7.62mm_Horizontal
R4: 1K; R_Axial_DIN0207_L6.3mm_D2.5mm_P10.16mm_Horizontal
R5: 2K; R_Axial_DIN0207_L6.3mm_D2.5mm_P15.24mm_Horizontal
R6, R8: 1.1K; R_Axial_DIN0207_L6.3mm_D2.5mm_P10.16mm_Horizontal
R7: 2K; R_Axial_DIN0207_L6.3mm_D2.5mm_P10.16mm_Horizontal
U1: LM7805_TO220; TO-220-3_Vertical
U2: NE5532; DIP-8_W7.62mm
U3: CB101

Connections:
+5V: C2.1, C3.1, U1.3 (VO), U2.8 (V+)
+12V: C1.1, J1.1, U1.1 (VI), U3.1 (VIN)
DAC_SIG: J1.3, U2.3 (+)
Earth: C1.2, C2.2, C3.2, D1.2 (A), J1.2, J1.7, R1.2, R3.1, R4.1, R6.1, R8.1, U1.2 (GND), U2.4 (V-), U3.2 (SGND), U3.3 (CGND)
IMON: R7.2, U3.6 (IMON)
IMON_3V3: J1.5, R7.1, R8.2
unnamed: D2.1 (K), R4.2
unnamed: D2.2 (A), U3.5 (VREF)
unnamed: J2.1, U3.8 (HV_RTIN)
unnamed: R1.1, R2.1, U2.2 (-)
VMON: D1.1 (K), R5.2, U3.7 (VMON)
VMON_3V3: J1.4, R5.1, R6.2
VPGM: J1.6, R2.2, R3.2, U2.1, U3.4 (VPGM)

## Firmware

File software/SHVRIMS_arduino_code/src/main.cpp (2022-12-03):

#include <Arduino.h>
#include <dac8568.h>
#include <LUT.h>
#include <SPI.h>

//********************** NANO33 BLE Pin ***************//
const int DAC_CS = 2; //D2
const int LDAC = 4; //D4
const int CLR = 3; //D3
const int SCKL = 13; //D13

const int ADC1_CS = A2; //A2
const int ADC2_CS = A1; //A1
const int ADC_MDAT = A0; //A0

uint32_t clockFreq = 2000000; 
uint16_t fullScaleDAC = 65535; //the scale of the DAC is 16 bit
uint16_t n = 16; //
float maxV = 15000.; //set maximum voltage
float desiredVoltage = 1000.; //set desired voltage


inline uint32_t DesiredVoltageInScale(float voltage)
{
  return uint32_t(float(fullScaleDAC) * voltage / maxV);
}

uint32_t voltageTo16bit(float voltage){
  return fullScaleDAC * voltage / maxV;
}

uint32_t desiredVoltageInScale =  DesiredVoltageInScale(2400.);
uint32_t desiredVoltageInScale2 = uint32_t(float(fullScaleDAC) * 2000 / maxV);

// 16 bit, 128 points normalized Look Up Table
uint16_t LUTSize = sizeof(SineWaveformNormalizedLUT) / sizeof(float);

// SPI Settings for DAC 
SPISettings DACsettings(clockFreq, MSBFIRST, SPI_MODE1); 
uint32_t messagetoDAC;

// SPI Settings for ADCs
SPISettings ADCsettings(10000000, MSBFIRST, SPI_MODE0); //10 mhz. ADC latches SDI on rising edge
SPISettings ADCsettingsRead(10000000, MSBFIRST, SPI_MODE1); //10 mhz. ADC latches SDO on falling edge. See page 66 datasheet

float desiredFrequency = 0.2;

uint32_t epsilonUs = 1000000. / (float(LUTSize) * desiredFrequency);


// Functions
void writetoDAC(uint32_t message);
float measureVoltage(int i){
  return analogRead(i);
}


int waitTime = 5000;
void measureResistance(int voltage){
  messagetoDAC = DAC8568_Write_Input_Reg_And_Update_Single(CH_C, voltageTo16bit(voltage));
  writetoDAC(messagetoDAC);
  delay(waitTime);
  Serial.print(voltage);
  Serial.print(" V - Measured Voltage on passive side: ");
  Serial.println(measureVoltage(A7)*3.3/4096, 5);
  delay(800);
}


//DAC functions
void writetoDAC(uint32_t message){
  digitalWrite(DAC_CS, LOW);
  SPI.beginTransaction(DACsettings);
  SPI.transfer(message >> 24);
  SPI.transfer(message >> 16);
  SPI.transfer(message >> 8);
  SPI.transfer(message);
  SPI.endTransaction();
  digitalWrite(DAC_CS, HIGH);
}

//DAC outputs
/*void squarewaveSingle(int amplitude, int frequency, int dutycycle, CHANNEL_SELECT channel){
  messagetoDAC = DAC8568_Write_Input_Reg_And_Update_Single(channel, SquareWaveEvenDutyCycleNormalizedLUT[]);
  writetoDAC(messagetoDAC);
}*/

void sinewavewithPhaseShift(){
    for (int i = 0; i < LUTSize; ++i)
  {
    messagetoDAC = DAC8568_Write_Input_Reg_And_Update_All(CH_G, SineWaveformNormalizedLUT[(i) % LUTSize] * desiredVoltageInScale);
    writetoDAC(messagetoDAC);
    messagetoDAC = DAC8568_Write_Input_Reg_And_Update_All(CH_E, SineWaveformNormalizedLUT[(i + 1 * n) % LUTSize] * desiredVoltageInScale);
    writetoDAC(messagetoDAC);
    messagetoDAC = DAC8568_Write_Input_Reg_And_Update_All(CH_A, SineWaveformNormalizedLUT[(i + 2 * n)  % LUTSize] * desiredVoltageInScale);
    writetoDAC(messagetoDAC);
    messagetoDAC = DAC8568_Write_Input_Reg_And_Update_All(CH_C, SineWaveformNormalizedLUT[(i + 3 * n)  % LUTSize] * desiredVoltageInScale);
    writetoDAC(messagetoDAC);
    messagetoDAC = DAC8568_Write_Input_Reg_And_Update_All(CH_H, SineWaveformNormalizedLUT[(i + 4 * n)  % LUTSize] * desiredVoltageInScale);
    writetoDAC(messagetoDAC);
    messagetoDAC = DAC8568_Write_Input_Reg_And_Update_All(CH_F, SineWaveformNormalizedLUT[(i + 5 * n)  % LUTSize] * desiredVoltageInScale);
    writetoDAC(messagetoDAC);
    messagetoDAC = DAC8568_Write_Input_Reg_And_Update_All(CH_D, SineWaveformNormalizedLUT[(i + 6 * n)  % LUTSize] * desiredVoltageInScale);
    writetoDAC(messagetoDAC);
    messagetoDAC = DAC8568_Write_Input_Reg_And_Update_All(CH_B, SineWaveformNormalizedLUT[(i + 7 * n)  % LUTSize] * desiredVoltageInScale);
    writetoDAC(messagetoDAC);
    
    delayMicroseconds(epsilonUs);
  }    
}

//ADC functions
void writetoADC2(uint16_t message){
  digitalWrite(ADC2_CS, LOW);
  SPI.beginTransaction(ADCsettings);
  //SPI.transfer(message >> 24);
  //SPI.transfer(message >> 16);
  //SPI.transfer(message >> 8);
  SPI.transfer16(message);
  //SPI.transfer(&message,4);
  SPI.endTransaction();
  digitalWrite(ADC2_CS, HIGH);
}

//ADC readings

void setup() {
  // put your setup code here, to run once:
  Serial.begin(9600);
  delay(2000);
  SPI.begin();

  pinMode(DAC_CS, OUTPUT);
  digitalWrite(DAC_CS, HIGH);
  delay(100);

  pinMode(LDAC, OUTPUT);
  digitalWrite(LDAC, LOW);
  delay(100);

  messagetoDAC = DAC8568_Setup(CONTROL_SETUP_FLEX_MODE, DATA_POWER_UP_INT_REF_ALWAYS_FLEX, FEATURE_POWER_UP_INT_REF_ALWAYS_FLEX);
  writetoDAC(messagetoDAC);
  delay(100);


  messagetoADC = 0b0101001011110000; //set config3. 32 bit DATA_FORMAT
  writetoADC2(messagetoADC);
  
  messagetoADC = 0b0100011011110011; //set config0. Internal Clock (bit 4-5: 11)
  writetoADC2(messagetoADC);
  
  messagetoADC = 0b0100101000001100; //select config1 + write to config1
  writetoADC2(messagetoADC);
  
  messagetoADC = 0b0100111010001011; //set config2
  writetoADC2(messagetoADC);

  messagetoADC = 0b0101011000000111; //set IRQ to inactive logic high(bit 2: 1)
  writetoADC2(messagetoADC);

  messagetoADC = 0b0101101000001000; //set MUX to CH0(bit4-8:0000) and AGND(bit 0-3:1000). See page 77 datasheet
  writetoADC2(messagetoADC);

  
}

int currentvoltage = 0;
int increment = 100;
bool setvoltageFlag = 0;
int setvoltage = 0;
int maxvoltage = 0;

void loop() {
  //Serial.println(epsilonUs);
  // put your main code here, to run repeatedly:
  delay(3000);
  while(setvoltageFlag == 0){
    Serial.println("Please set the voltage increment");
    while(Serial.available() == 0);
    increment = Serial.parseInt();
    Serial.println(increment);
    Serial.parseInt();
    
    Serial.println("Please set the maximum voltage");
    while(Serial.available() == 0){;}
    maxvoltage = Serial.parseInt();
    Serial.println(maxvoltage);
    Serial.parseInt();

    Serial.println("Please set the time delay(in milliseconds) between voltage change and measure");
    while(Serial.available() == 0){;}
    waitTime = Serial.parseInt();
    Serial.println(waitTime);
    Serial.parseInt();

    setvoltageFlag = 1;
  }

  for (currentvoltage = 0; currentvoltage <= maxvoltage; currentvoltage += increment){
    measureResistance(currentvoltage);
    if(Serial.read() == 'p'){
      Serial.println("Press 'r' to resume");
      while(Serial.read() != 'r');
    }
  }

  for (currentvoltage = maxvoltage; currentvoltage >= 0; currentvoltage -= increment){
    measureResistance(currentvoltage);
    if(Serial.read() == 'p'){
      Serial.println("Press 'r' to resume");
      while(Serial.read() != 'r');
    }
  }

}

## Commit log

2022-06-17 altium to kicad schematics
    [revised_minh_design.kicad_pcb, revised_minh_design.kicad_sch]
2022-06-18 libraries and footprints
    [CB101.STEP, revised_minh_design.kicad_pcb, revised_minh_design.kicad_sch]
2022-06-22 HV Module routed, some footprint changes
    [revised_minh_design.kicad_pcb, revised_minh_design.kicad_sch]
2022-06-22 components routing mostly finished for DAC/ADC board
    [revised_minh_design.kicad_pcb]
2022-06-22 minor adjustments
    [revised_minh_design.kicad_pcb]
2022-06-23 resolved DRC errors and most warnings
    [revised_minh_design.kicad_pcb]
2022-06-23 DAC ground to AGND, new AGND polygon pour
    [revised_minh_design.kicad_pcb, revised_minh_design.kicad_sch]
2022-06-24 Split ground plane design with no errors
    [revised_minh_design.kicad_pcb]
2022-06-24 Fab ready version with joined ground plane, extra caps for ADCs
    [revised_minh_design.kicad_pcb, revised_minh_design.kicad_sch]
2022-06-24 Repositioned clock closer
    [revised_minh_design.kicad_pcb]
2022-06-25 JLCPB Submission. Name added, connectors changed to double layer
    [revised_minh_design.kicad_pcb, revised_minh_design.kicad_sch]
2022-06-25 JLCPB Submission. Name added, connectors changed to double layer, rounded corners
    [revised_minh_design.kicad_pcb]
2022-06-25 Added NANO33 BLE footprint, and stiching vias near mcu
    [revised_minh_design.kicad_pcb]
2022-06-25 JLCPCB submission for dual MCU design
    [CB101.STEP, HV revised_minh_design.csv, revised_minh_design-B_Cu.gbr, revised_minh_design-B_Mask.gbr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]
2022-06-28 New HV board for 15A12
2022-06-28 JLCPCB Submission for 15A12 board
    [Adapter.kicad_pcb, Adapter.kicad_sch, revised_minh_design-B_Cu.gbr, revised_minh_design-B_Mask.gbr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]
2022-06-29 JLCPCB Submission for 15A12 board, double row connectors added, separate power and signal connectors
    [revised_minh_design-B_Cu.gbr, revised_minh_design-B_Mask.gbr, revised_minh_design-B_Paste.gbr, revised_minh_design-B_Silkscreen.gbr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]
2022-06-29 new diagrams and adapter board
    [CB101.STEP, OL-015_15A_STANDARD.stp, revised_minh_design-B_Cu.gbr, revised_minh_design-B_Mask.gbr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]
2022-06-29 adapter board 4 layers
    [revised_minh_design.kicad_pcb, revised_minh_design.kicad_sch]
2022-07-10 exported STEP file. Minor changes to schematics for better documentations
    [revised_minh_design-B_Cu.gbr, revised_minh_design-B_Mask.gbr, revised_minh_design-B_Paste.gbr, revised_minh_design-B_Silkscreen.gbr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]
2022-09-20 reordering files, added plotting web plotting stuff
    [CB101.STEP, HV revised_minh_design.csv, OL-015_15A_STANDARD.stp, revised_minh_design-B_Cu.gbr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]
2022-09-22 DAC software arduino
2022-09-22 further DAC setup arduino code
2022-09-24 Fixed PI PO, DAC port ordering, MDAT Pin, clock connection
    [revised_minh_design.kicad_pcb, revised_minh_design.kicad_sch]
2022-09-24 Used 2nd opamp for unity gain on VMON
    [revised_minh_design.kicad_pcb, revised_minh_design.kicad_sch]
2022-09-24 routed the netlist for ADC/DAC v2
    [OL-015_15A_STANDARD.stp, revised_minh_design.kicad_pcb, revised_minh_design.kicad_sch]
2022-09-25 software update, added some diagrams
    [revised_minh_design.csv]
2022-09-25 added BOM Excel
    [SHVRIMPS_BOM.xlsx, revised_minh_design.csv, revised_minh_design.kicad_pcb, revised_minh_design.kicad_sch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]
2022-10-01 edited videos, updated BOM, added Matlab plots
    [SHVRIMPS_BOM.xlsx]
2022-12-03 hardware update to add GPIO directly to MCU
    [revised_minh_design.kicad_pcb, revised_minh_design.kicad_sch]
